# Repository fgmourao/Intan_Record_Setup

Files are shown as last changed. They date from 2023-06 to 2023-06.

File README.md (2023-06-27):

# A Fully Adapted Headstage With Custom Electrode Arrays Designed for Electrophysiological Experiments<br />

Front. Neurosci., 03 March 2022<br />
Sec. Neural Technology <br />
https://doi.org/10.3389/fnins.2021.691788<br />

Correspondence:<br />

Flávio Afonso Gonçalves Mourão, PhD<br />
Núcleo de Neurociências, Departamento de Fisiologia e Biofísica<br />
Instituto de Ciências Biológicas (ICB)<br /> 
Universidade Federal de Minas Gerais (UFMG)<br />
Av. Antônio Carlos, 6627 - CEP 31270-901- Campus Pampulha<br />
Belo Horizonte - MG - Brazil<br />
Fax: +55 31 3409-2924 Phone: +55 31 3409-2927<br />
Email:  mourao.fg@gmail.com / fagm@ufmg.br <br />

Márcio Flávio Dutra Moraes, PhD<br />
Núcleo de Neurociências, Departamento de Fisiologia e Biofísica<br />
Instituto de Ciências Biológicas (ICB)<br /> 
Universidade Federal de Minas Gerais (UFMG)<br />
Av. Antônio Carlos, 6627 - CEP 31270-901- Campus Pampulha<br />
Belo Horizonte - MG - Brazil<br />
Fax: +55 31 3409-2924 Phone: +55 31 3409-2930<br />
Email: mfdm@icb.ufmg.br <br />
<br />

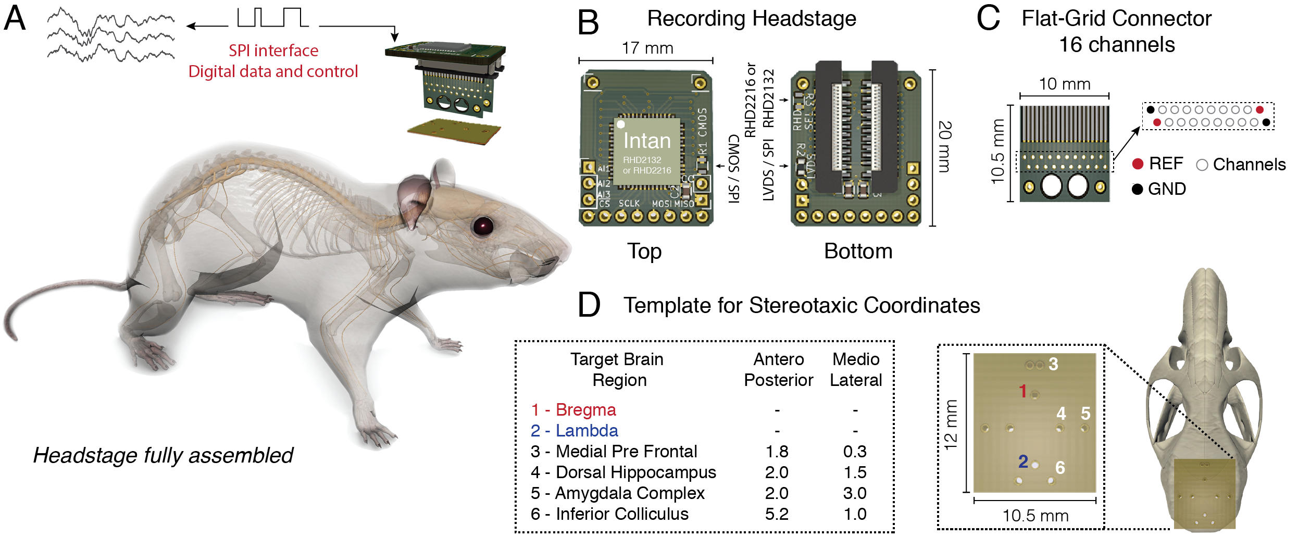
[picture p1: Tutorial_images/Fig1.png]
<br />

Headstage adapted from the Intan RHD headstage system with a flexible printed circuit (SMD/FPC) connector. A) Headstage fully assembled in real size. B) Top and bottom view of the headstage. Both the 2132 and 2216 Intan chips can be used according to the circuit configuration chosen. C) Flat-Grid connector board for sixteen channels designed to connect to the SMD/FPC connector. D) Fiber board punctured with small holes according to the chosen stereotaxic coordinates. A variable number of electrodes can be aligned and fixed from distinct dorsoventral configurations.

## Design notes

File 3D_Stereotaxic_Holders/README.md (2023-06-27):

# 3D Holders <br />

Support base to hold the fiber board <br />

https://github.com/fgmourao/Lab_Projects/blob/master/Intan%20Record%20Setup/Tutorial_images/1.png<br />

Support base to hold both the flat-grid connector and the fiber board <br />
https://github.com/fgmourao/Lab_Projects/blob/master/Intan%20Record%20Setup/Tutorial_images/0.png

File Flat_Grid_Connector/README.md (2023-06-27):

# Flat-Grid Connector <br />

V2 - Current Version<br />

https://github.com/fgmourao/Lab_Projects/blob/master/Intan%20Record%20Setup/Tutorial_images/Channels_Map_V2_Current_Version.png<br />

V1 - Old Version<br />

https://github.com/fgmourao/Lab_Projects/blob/master/Intan%20Record%20Setup/Tutorial_images/Channels_Map_V1_Old_Version.png<br />

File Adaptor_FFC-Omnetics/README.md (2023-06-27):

# Adapters

RHD 16-Channel Recording Headstages<br />

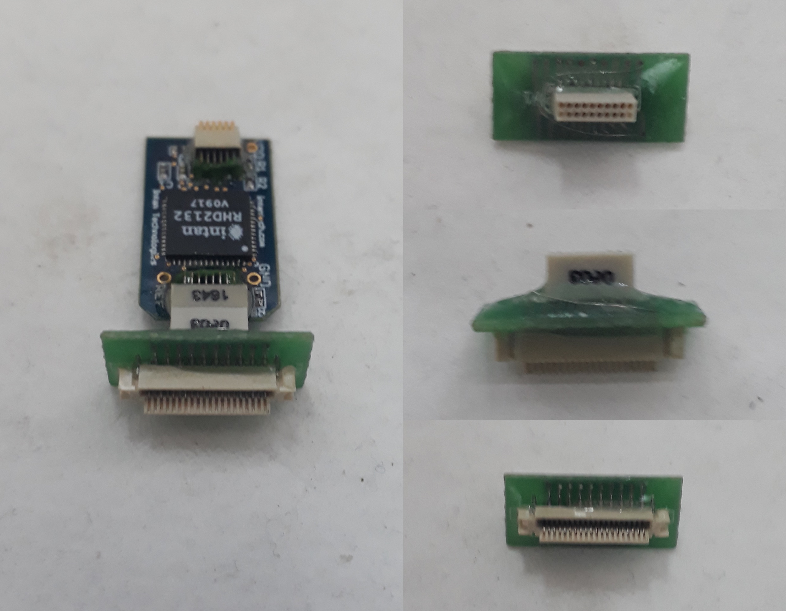
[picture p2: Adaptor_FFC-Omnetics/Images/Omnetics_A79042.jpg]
https://github.com/fgmourao/Lab_Projects/blob/master/Intan%20Record%20Setup/Adaptor_FFC-Omnetics/Images/Omnetics_A79042.jpg
<br />

RHD 32-Channel Recording Headstages<br />

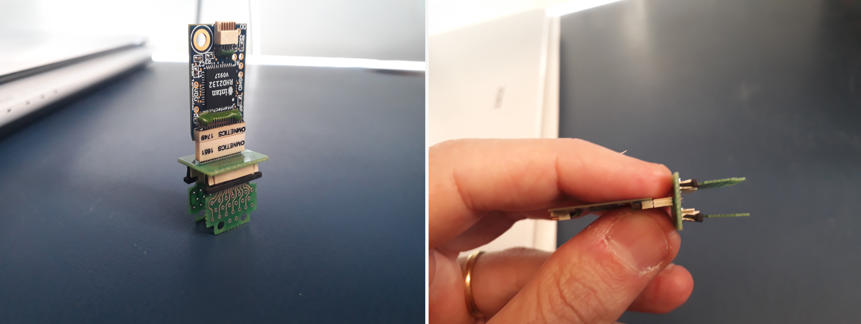
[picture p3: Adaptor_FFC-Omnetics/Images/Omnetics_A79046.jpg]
https://github.com/fgmourao/Lab_Projects/blob/master/Intan%20Record%20Setup/Adaptor_FFC-Omnetics/Images/Omnetics_A79046.jpg
<br />

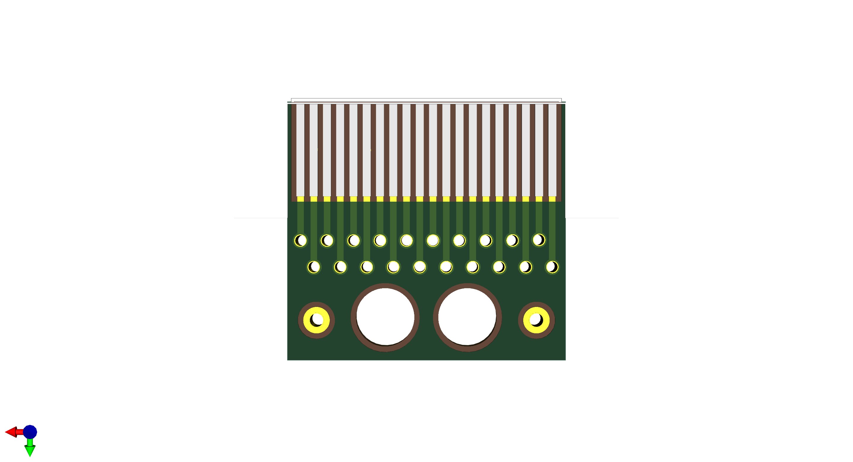
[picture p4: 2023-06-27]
Flat_Grid_Connector/V2/Schematic_PCB/Images/Flat_Grid_Small_V2.png

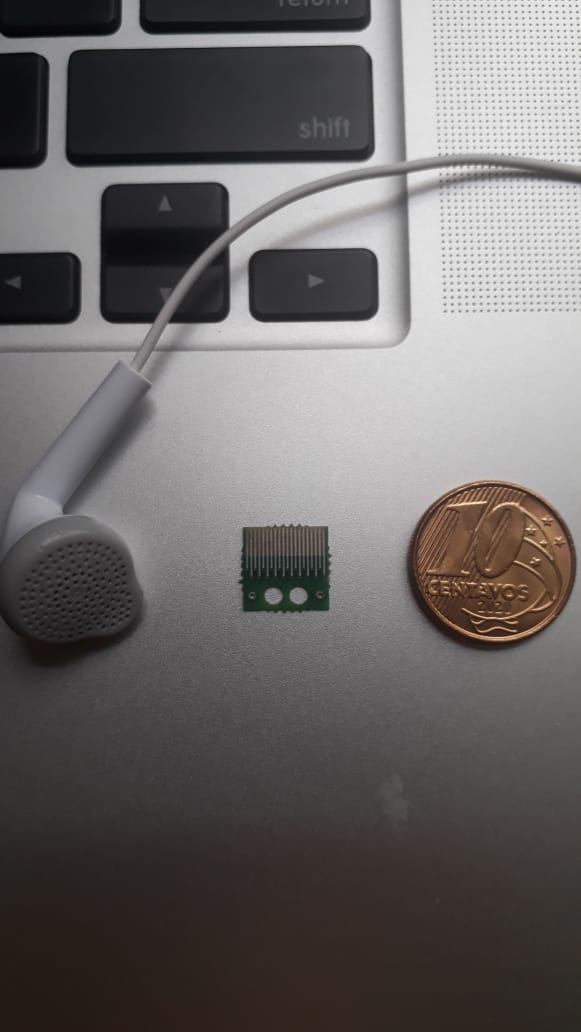
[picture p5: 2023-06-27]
Flat_Grid_Connector/V2/Schematic_PCB/Images/2021-03-30 at 17.20.01.png

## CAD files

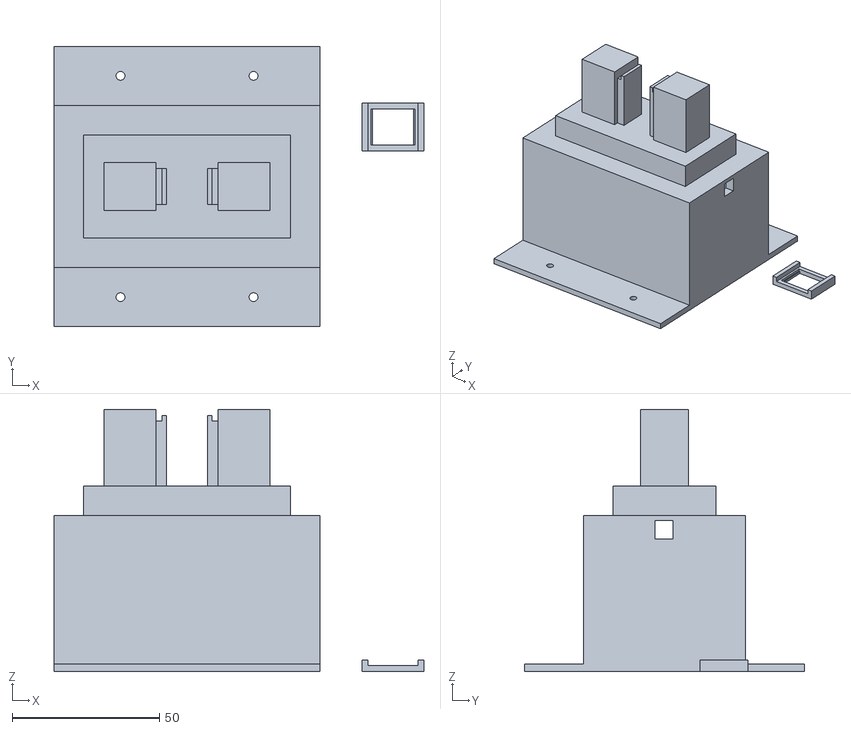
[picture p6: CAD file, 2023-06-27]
3D_Stereotaxic_Holders/Board_Stx_holder_rats.stl
125.4 x 95.0 x 88.9

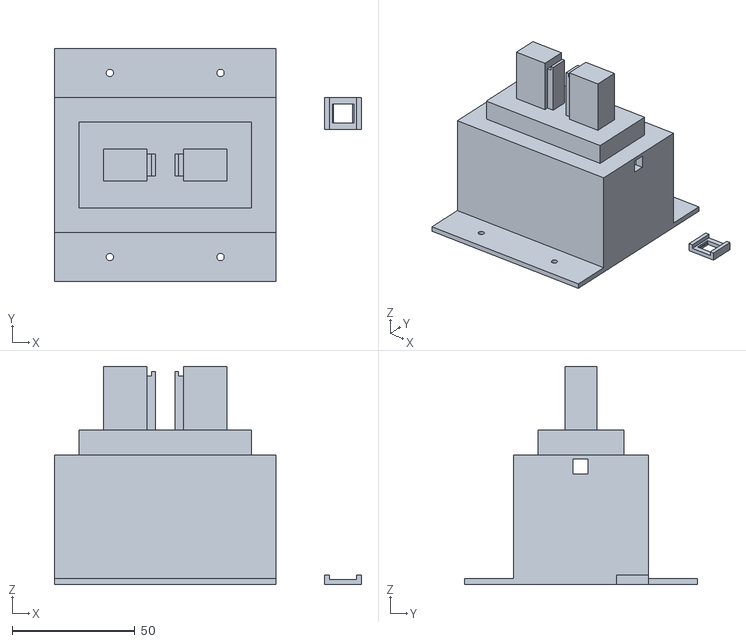
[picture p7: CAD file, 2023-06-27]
3D_Stereotaxic_Holders/Board_Stx_holder_mice.stl
125.1 x 95.0 x 88.9

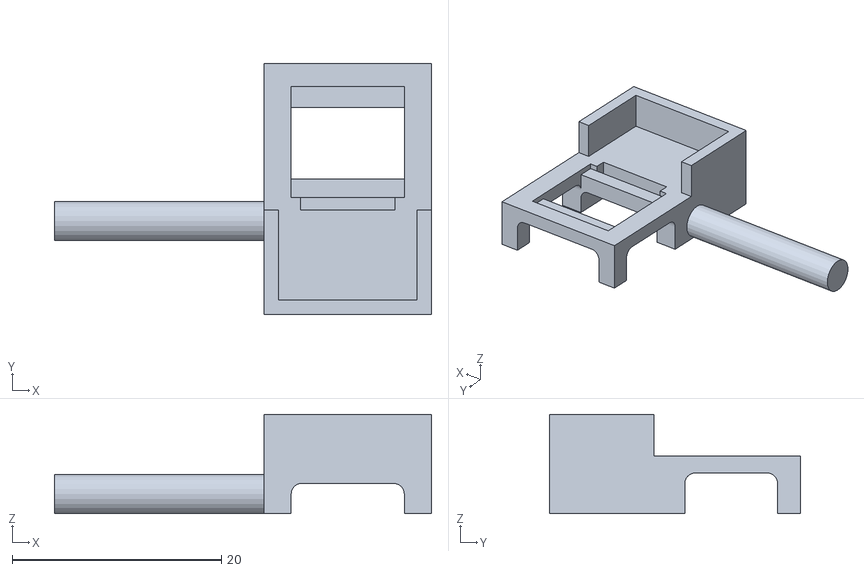
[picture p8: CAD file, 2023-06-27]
3D_Stereotaxic_Holders/Flat_template_holder.stl
36.0 x 24.0 x 9.50

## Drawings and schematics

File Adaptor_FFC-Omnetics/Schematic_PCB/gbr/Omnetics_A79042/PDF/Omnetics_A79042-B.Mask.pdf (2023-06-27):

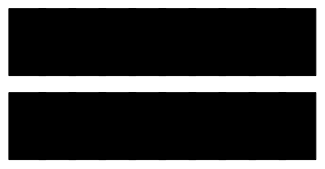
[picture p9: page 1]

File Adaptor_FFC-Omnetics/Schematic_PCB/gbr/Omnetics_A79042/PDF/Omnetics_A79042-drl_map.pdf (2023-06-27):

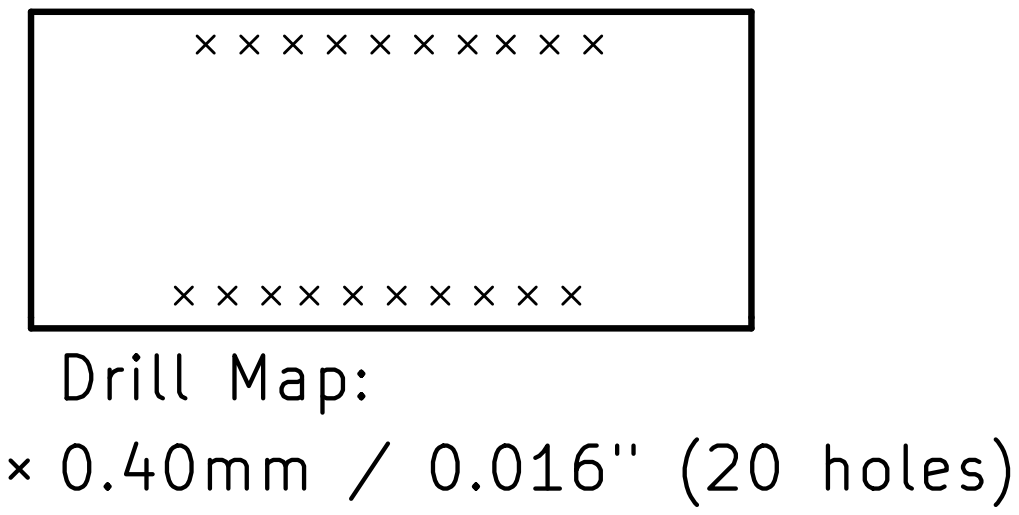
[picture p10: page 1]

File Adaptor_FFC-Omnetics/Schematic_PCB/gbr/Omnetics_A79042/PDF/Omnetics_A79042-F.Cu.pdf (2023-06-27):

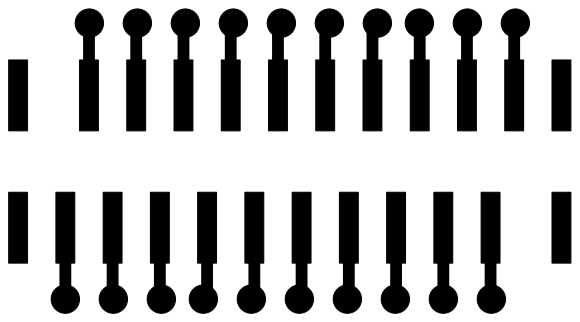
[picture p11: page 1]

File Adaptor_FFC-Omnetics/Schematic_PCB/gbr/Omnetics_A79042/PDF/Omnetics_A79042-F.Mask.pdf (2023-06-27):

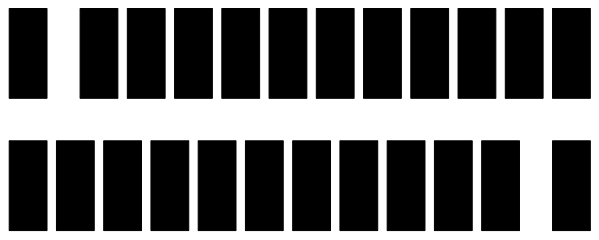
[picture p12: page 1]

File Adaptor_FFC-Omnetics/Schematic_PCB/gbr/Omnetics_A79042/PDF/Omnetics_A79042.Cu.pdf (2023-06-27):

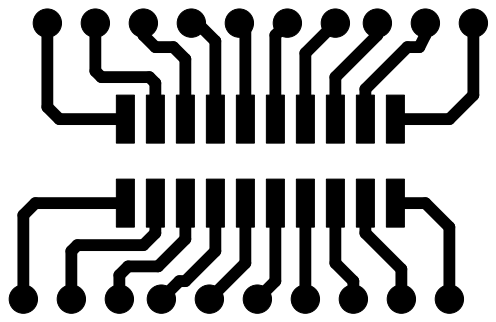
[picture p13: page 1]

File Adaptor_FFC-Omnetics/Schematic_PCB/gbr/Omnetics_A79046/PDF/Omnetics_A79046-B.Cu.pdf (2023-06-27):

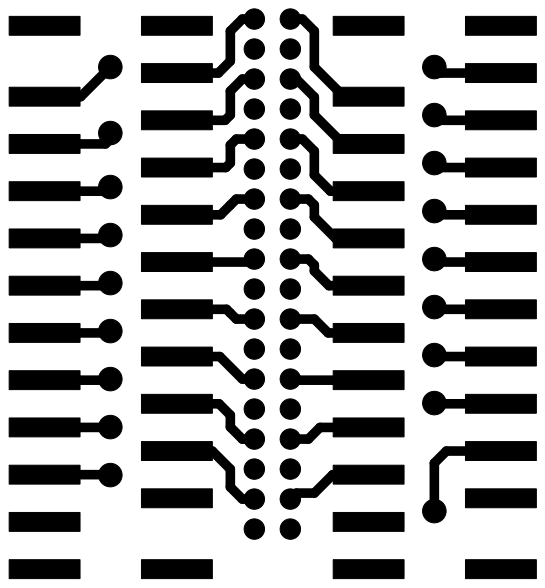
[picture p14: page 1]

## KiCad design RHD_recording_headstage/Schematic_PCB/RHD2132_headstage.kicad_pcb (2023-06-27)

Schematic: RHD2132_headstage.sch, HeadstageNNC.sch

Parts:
C1, C3: 100n; R_0603
C2: 10n; R_0603
J1, J2: FFCfemale20
J3: AuxInputs; Pin_Header_Straight_1x03_Pitch2.00mm
J4: SPI; JumperSPI2
J5: POWER; Pin_Header_Straight_1x02_Pitch2.00mm
J6, J7: Conn_01x01; Pin_Header_Straight_1x01_Pitch2.00mm
R1, R2, R3: 0; R_0603
U1: RHD2132_QFN; RHD2000-QFN56_8_X_8_LARGE

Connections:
/N$42: C2.1, U1.28 (ADC_REF)
/N$43: U1.27 (AUXOUT)
AUXIN1: J3.1, U1.14 (AUXIN1)
AUXIN2: J3.2, U1.15 (AUXIN2)
AUXIN3: J3.3, U1.16 (AUXIN3)
CH0: J1.3, U1.9 (IN0)
CH1: J1.4, U1.8 (IN1)
CH2: J1.5, U1.7 (IN2)
CH3: J1.6, U1.6 (IN3)
CH4: J1.7, U1.5 (IN4)
CH5: J1.8, U1.4 (IN5)
CH6: J1.9, U1.3 (IN6)
CH7: J1.10, U1.2 (IN7)
CH8: J1.11, U1.1 (IN8)
CH9: J1.13, U1.56 (IN9)
CH10: J1.15, U1.55 (IN10)
CH11: J1.17, U1.54 (IN11)
CH12: J1.16, U1.53 (IN12)
CH13: J1.18, U1.52 (IN13)
CH14: J1.14, U1.51 (IN14)
CH15: J1.12, U1.50 (IN15)
CH16: J2.13, U1.49 (IN16)
CH17: J2.17, U1.48 (IN17)
CH18: J2.15, U1.47 (IN18)
CH19: J2.18, U1.46 (IN19)
CH20: J2.16, U1.45 (IN20)
CH21: J2.14, U1.44 (IN21)
CH22: J2.12, U1.43 (IN22)
CH23: J2.11, U1.42 (IN23)
CH24: J2.10, U1.41 (IN24)
CH25: J2.9, U1.40 (IN25)
CH26: J2.8, U1.39 (IN26)
CH27: J2.7, U1.38 (IN27)
CH28: J2.6, U1.37 (IN28)
CH29: J2.5, U1.36 (IN29)
CH30: J2.4, U1.35 (IN30)
CH31: J2.3, U1.34 (IN31)
GND: C1.2, C2.2, C3.2, J1.1, J1.20, J2.1, J2.20, J5.1, R1.1, R3.1, U1.11 (GND1), U1.12 (GND2), U1.17 (GND3), U1.29 (GND4), U1.32 (VESD), U1.CENT (CTR)
MISO+: J4.8, U1.25 (MISO+)
MISO-: J4.7, U1.24 (MISO-)
MOSI+: J4.6, U1.23 (MOSI+)
MOSI-: J4.5, U1.22 (MOSI-)
unnamed: R1.2, R2.2, U1.30 (LVDS_EN)
REF_ELECTRODE: J1.2, J1.19, J2.2, J2.19, R3.2, U1.10 (REF_ELEC)
SCLK+: J4.4, U1.21 (SCLK+)
SCLK-: J4.3, U1.20 (SCLK-)
VCC: C1.1, C3.1, J5.2, R2.1, U1.13 (VDD1), U1.26 (VDD2), U1.31 (VDD3)
~CS~+: J4.2, U1.19 (~CS~+)
~CS~-: J4.1, U1.18 (~CS~-)

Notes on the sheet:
RHD2132 Intan Chip
FFC Connectors
Select between LVDS and CMOS
Jumpers
Mechanical support
LVDS
CMOS
Select between RHD2216 and RHD2132
This resistor must be soldered when using RHD2216.
Unconnected

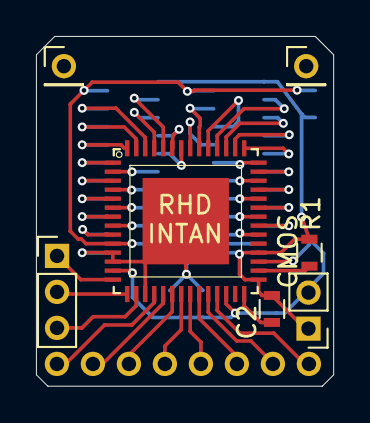
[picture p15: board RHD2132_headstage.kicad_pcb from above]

Board: 4 copper layers, 16.5 x 19.4 mm, 14 parts (0 on the bottom side), 48 nets.

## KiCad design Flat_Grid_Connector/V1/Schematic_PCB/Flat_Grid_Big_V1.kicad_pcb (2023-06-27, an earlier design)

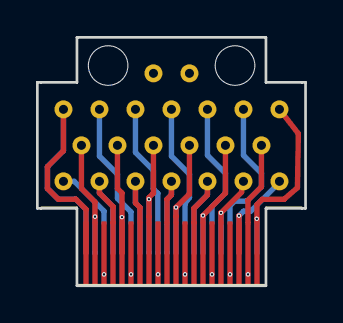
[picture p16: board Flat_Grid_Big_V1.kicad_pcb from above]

Board: 2 copper layers, 14.9 x 13.8 mm, 3 parts (1 on the bottom side), 20 nets.

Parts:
Edge1, Edge2: Conn_01x20; FFCmale20_semvias
Holes1: Conn_01x20; FFCmalePINarray

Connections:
unnamed: Edge1.1, Edge2.20, Holes1.1
unnamed: Edge1.2, Edge2.19, Holes1.2
unnamed: Edge1.3, Edge2.18, Holes1.3
unnamed: Edge1.4, Edge2.17, Holes1.4
unnamed: Edge1.5, Edge2.16, Holes1.5
unnamed: Edge1.6, Edge2.15, Holes1.6
unnamed: Edge1.7, Edge2.14, Holes1.7
unnamed: Edge1.8, Edge2.13, Holes1.8
unnamed: Edge1.9, Edge2.12, Holes1.9
unnamed: Edge1.10, Edge2.11, Holes1.10
unnamed: Edge1.11, Edge2.10, Holes1.11
unnamed: Edge1.12, Edge2.9, Holes1.12
unnamed: Edge1.13, Edge2.8, Holes1.13
unnamed: Edge1.14, Edge2.7, Holes1.14
unnamed: Edge1.15, Edge2.6, Holes1.15
unnamed: Edge1.16, Edge2.5, Holes1.16
unnamed: Edge1.17, Edge2.4, Holes1.17
unnamed: Edge1.18, Edge2.3, Holes1.18
unnamed: Edge1.19, Edge2.2, Holes1.19
unnamed: Edge1.20, Edge2.1, Holes1.20

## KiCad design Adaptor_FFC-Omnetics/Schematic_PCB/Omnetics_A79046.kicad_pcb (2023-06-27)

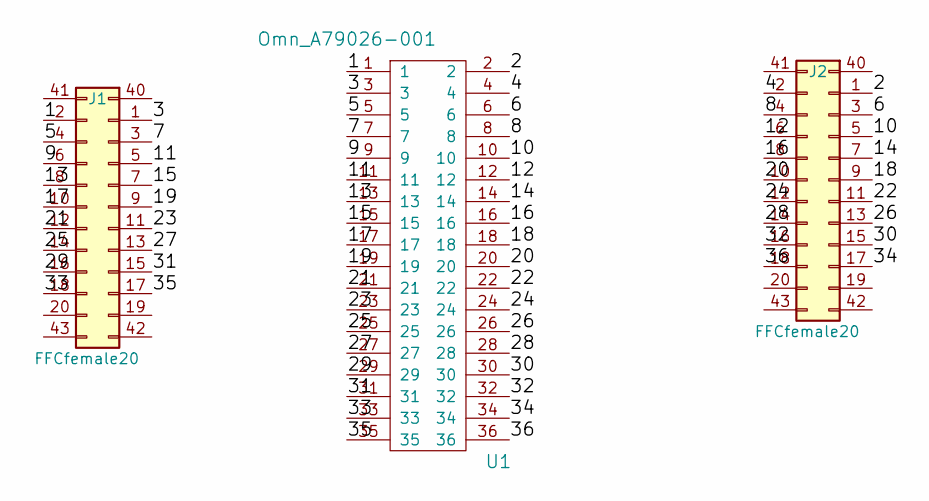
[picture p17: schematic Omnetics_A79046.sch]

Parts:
J1, J2: FFCfemale20
U1: Omn_A79026-001; Omn_A79026_pin

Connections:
/1: J1.2, U1.1
/2: J2.1, U1.2
/3: J1.1, U1.3
/4: J2.2, U1.4
/5: J1.4, U1.5
/6: J2.3, U1.6
/7: J1.3, U1.7
/8: J2.4, U1.8
/9: J1.6, U1.9
/10: J2.5, U1.10
/11: J1.5, U1.11
/12: J2.6, U1.12
/13: J1.8, U1.13
/14: J2.7, U1.14
/15: J1.7, U1.15
/16: J2.8, U1.16
/17: J1.10, U1.17
/18: J2.9, U1.18
/19: J1.9, U1.19
/20: J2.10, U1.20
/21: J1.12, U1.21
/22: J2.11, U1.22
/23: J1.11, U1.23
/24: J2.12, U1.24
/25: J1.14, U1.25
/26: J2.13, U1.26
/27: J1.13, U1.27
/28: J2.14, U1.28
/29: J1.16, U1.29
/30: J2.15, U1.30
/31: J1.15, U1.31
/32: J2.16, U1.32
/33: J1.18, U1.33
/34: J2.17, U1.34
/35: J1.17, U1.35
/36: J2.18, U1.36

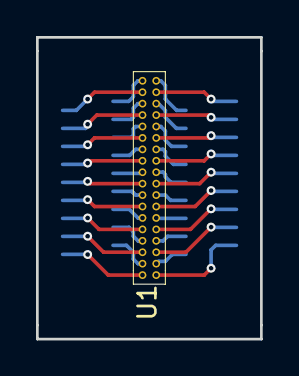
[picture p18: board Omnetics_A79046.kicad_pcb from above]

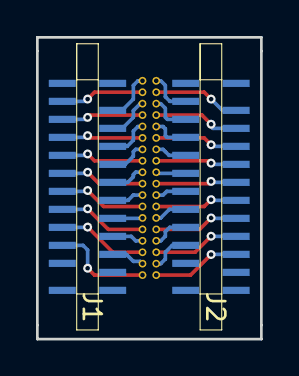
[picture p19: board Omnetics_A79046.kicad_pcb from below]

Board: 2 copper layers, 12.4 x 16.8 mm, 3 parts (2 on the bottom side), 36 nets.

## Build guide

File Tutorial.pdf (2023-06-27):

A fully adapted headstage for electrophysiological experiments with custom and scalable electrode arrays to record widely distributed brain regions.

Supplementary Material – Tutorials

Authors: Flávio Afonso Gonçalves Mourãoa

, Leonardo de Oliveira Guarnieri ab, Paulo Aparecido Amaral Júnior ab, Vinícius Rezende Carvalho ab

, Eduardo Mazoni Andrade Marçal Mendes ab, Márcio Flávio Dutra Moraes a
a. Núcleo de Neurociências, Departamento de Fisiologia e Biofísica, Instituto de Ciências Biológicas (ICB), Universidade Federal de Minas Gerais (UFMG). Av. Antônio Carlos, 6627 - CEP 31270-901. Belo Horizonte, Minas Gerais, Brazil.
b. Programa de Pós-Graduação em Engenharia Elétrica, Departamento de Engenharia Eletrônica (DELT), Escola de Engenharia, Universidade Federal de Minas Gerais (UFMG). Av. Antônio Carlos, 6627 - CEP 31270-901. Belo Horizonte, Minas Gerais, Brazil.

Correspondence:

Flávio Afonso Gonçalves Mourão, PhD Email: fagm@ufmg.br

Márcio Flávio Dutra Moraes, PhD Email: mfdm@icb.ufmg.br

2021

Recording Headstage

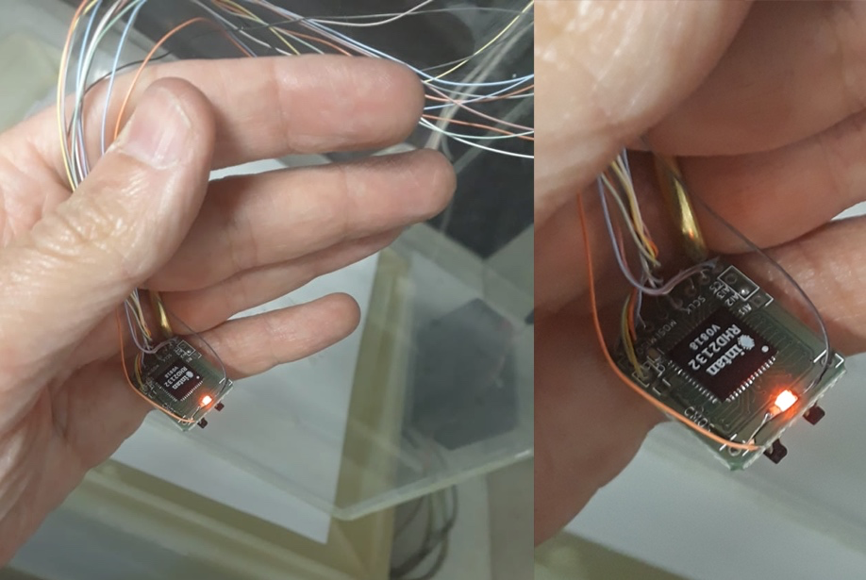
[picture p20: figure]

* Led is not in the original project

Component | Specification | Supplier | Price | Quantity | Link
FPC connector (Flexible Printed Circuits) | SMD vertical type 0.5mm pitch 2mm height | mktechnic | $0.79(un) | 2 | https://cutt.ly/Xx55qQE
RHD2132 amplifier chip | 32-channel unipolar inputs and common reference | Intan Technologies | $390 (un) | 1 | https://cutt.ly/Yx6qief
RHD2216 amplifier chip | 16-channel differential inputs | Intan Technologies | $260 (un) | 1 | https://cutt.ly/Yx6qief
Resistor | SMD – 0 W | Digikey | $0.22(un) | 1 | https://www.digikey.com
Capacitor | SMD – 10 nF | Digikey | $0.17(un) | 1 | https://www.digikey.com
Capacitor | SMD – 100 nF | Digikey | $0.17(un) | 2 | https://www.digikey.com

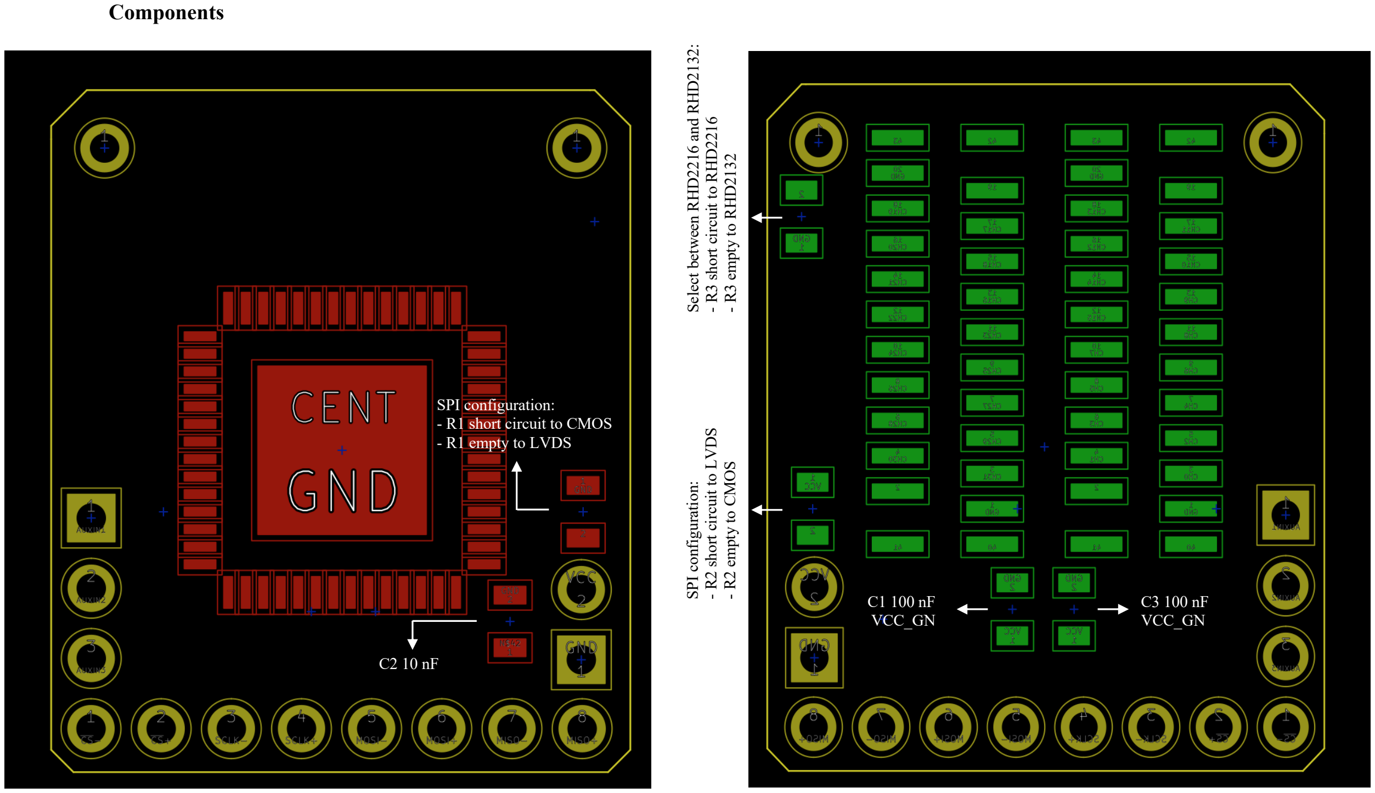
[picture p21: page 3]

Components

SPI configuration: - R1 short circuit to CMOS - R1 empty to LVDS

C2 10 nF

Select between RHD2216 and RHD2132:

- R3 short circuit to RHD2216
- R3 empty to RHD2132

SPI configuration:

- R2 short circuit to LVDS
- R2 empty to CMOS

C1 100 nF
VCC_GN

C3 100 nF
VCC_GN

Handmade cable

We strongly recommend the following tutorial:

- https://open-ephys.atlassian.net/wiki/spaces/OEW/pages/491587/Fine+wire+tether
Component | Specification | Supplier | Price | Quantity | Link
Omnetics Polarized PZN | Straight Thru-Hole (Type DD) 12 contacts | Omnetics Connector Corporation | on request ~$40 (un) | 1 | https://cutt.ly/FcqiCNQ
Micro bare copper wire | CZ 1187 wire series | Cooner Wire | on request | 1 | https://cutt.ly/lcqo9Pz

However, in our adapted board, each contact needs to be checked

Wiring diagram:

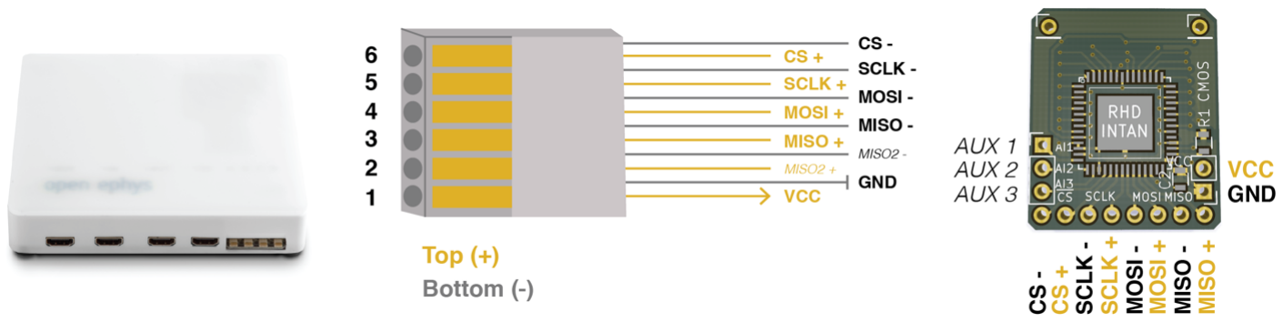
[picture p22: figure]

Flat-Grid Connector – V2 – Current Version

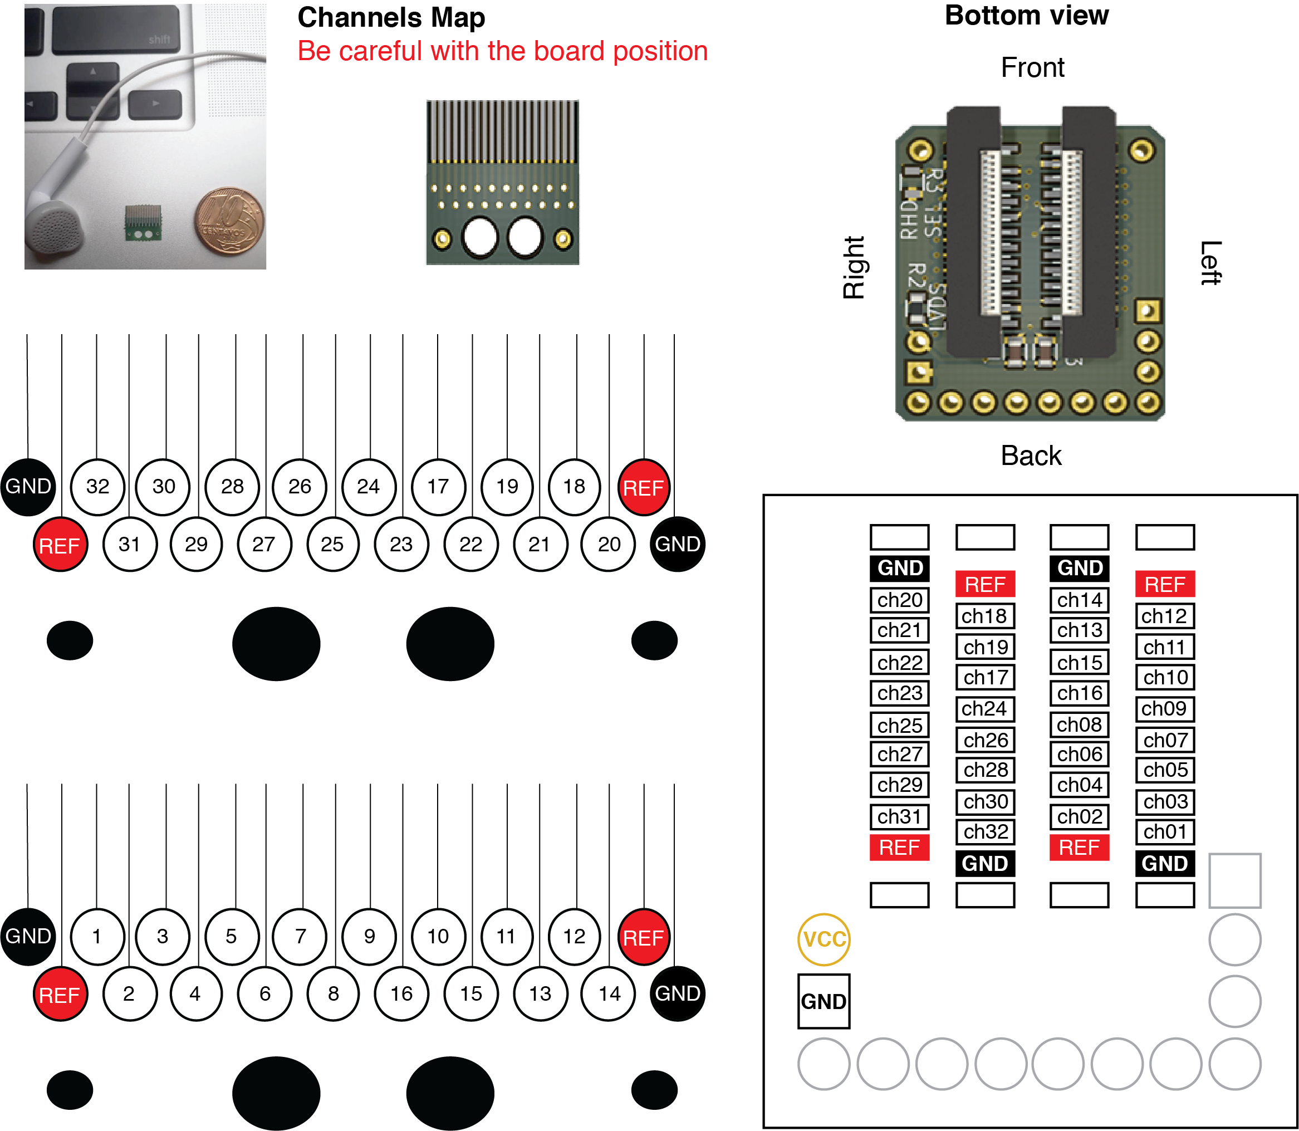
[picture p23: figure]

Component | Specification | Supplier | Price | Quantity | Link
Stainless steel wire | 0.127 mm internal diameter, teflon-coated. 100 feet. Model 7914 | A-M Systems Inc | $140 (un) | 1 | https://cutt.ly/5x6eIoR
Tungsten microwires | 99.5% S-Formvar 50 µm ID | California Fine Wire Co. | on request | - | https://cutt.ly/FbJxLBi
Silver paint | 1 troy oz. (31.1g) | SPI SuppliesⓇ | ~$50 (un) | 1 | https://cutt.ly/Ox6sup1
Thermosetting polymer | 5 minute Epoxy | Devcon | ~$20 (un) | 1 | https://cutt.ly/Zx6ltrEhttps://cutt.ly/mx6zobJhttps://cutt.ly/Rx6zFZZ
Scissors | Tungsten Carbide 3.5 inches | Dr. Slick Co. | ~$30 (un) | 1 | https://www.drslick.com

Flat-Grid Connector – V1 – Old Version

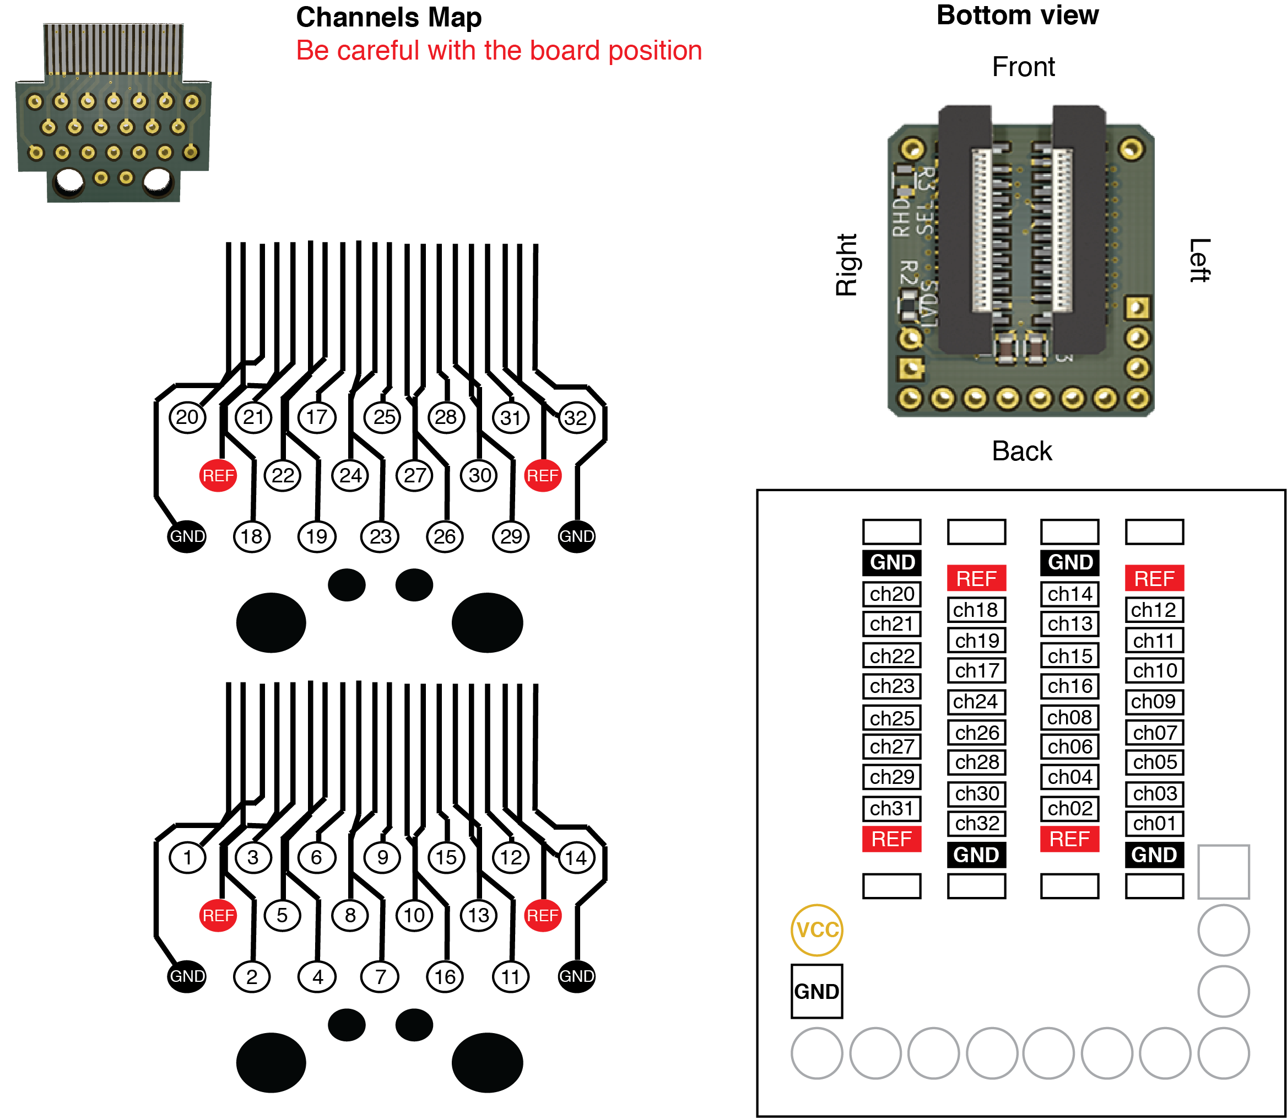
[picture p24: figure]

SMD/FPC connector ß à Omnetics
Adapters for the original RHD headstage
Component | Specification | Supplier | Price | Quantity | Link
FPC connector (Flexible Printed Circuits) | SMD vertical type 0.5mm pitch 2mm height | mktechnic | $0.79(un) | 2 | https://cutt.ly/Xx55qQE
Omnetics Neuro Nano Strip | A79042-001 NPD-18-VV-GS | Omnetics Connector Corporation | on request ~$60 (un) | 1 | https://cutt.ly/UcqDO66
Omnetics Neuro Nano Strip | A79046-001 NPD-36-DD-GS | Omnetics Connector Corporation | on request ~$90 (un) | 1 | https://cutt.ly/UcqDO66

RHD 16-Channel Recording Headstages

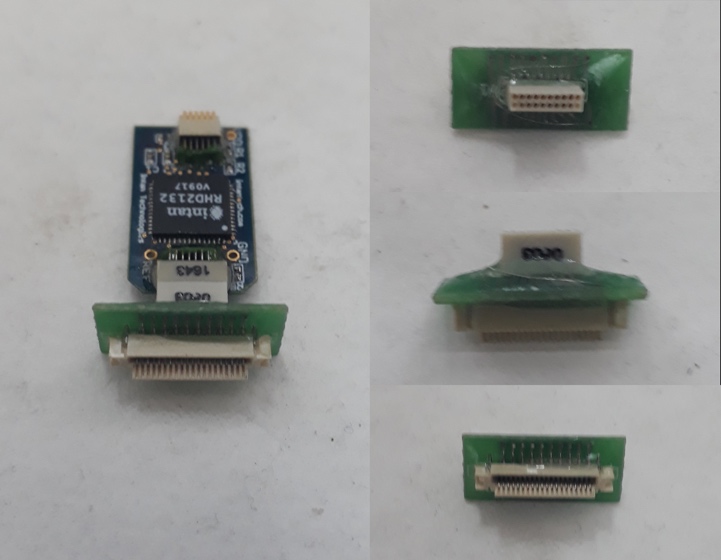
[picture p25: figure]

RHD 32-Channel Recording Headstages

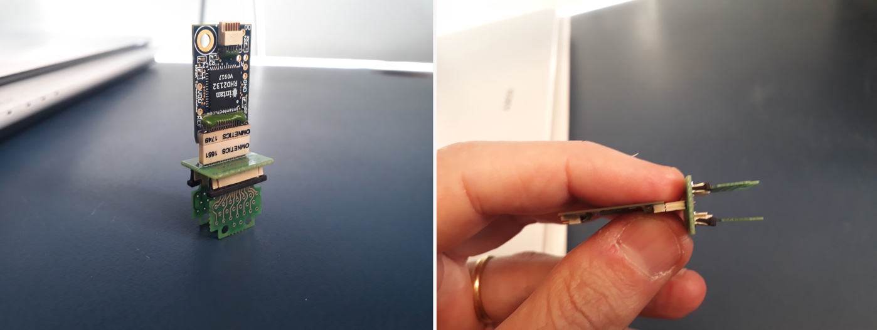
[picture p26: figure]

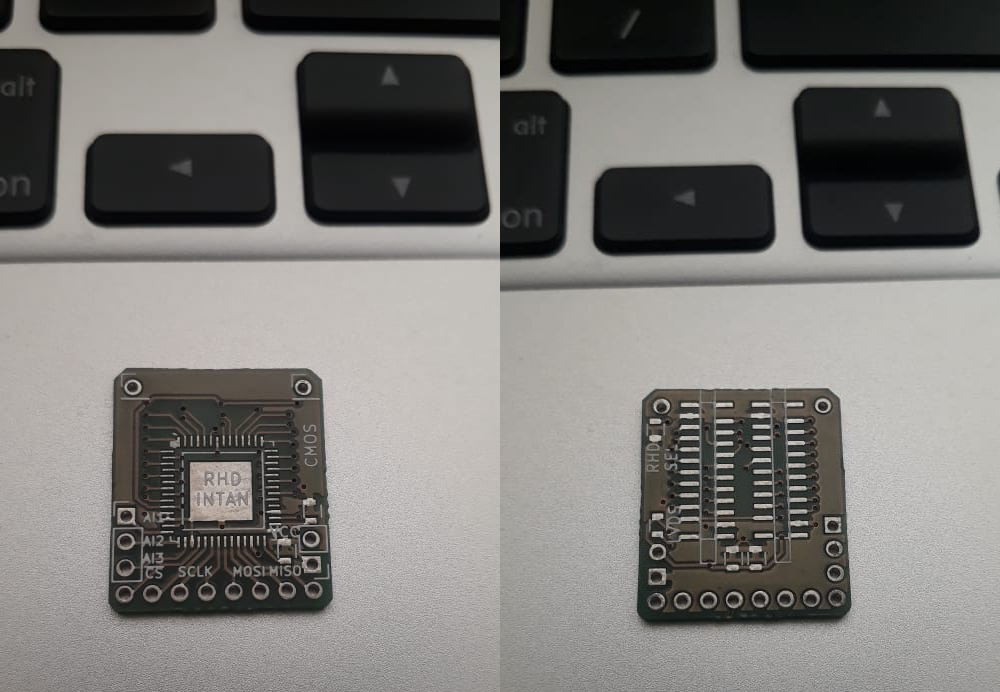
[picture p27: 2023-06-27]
Tutorial_images/headstage2.png

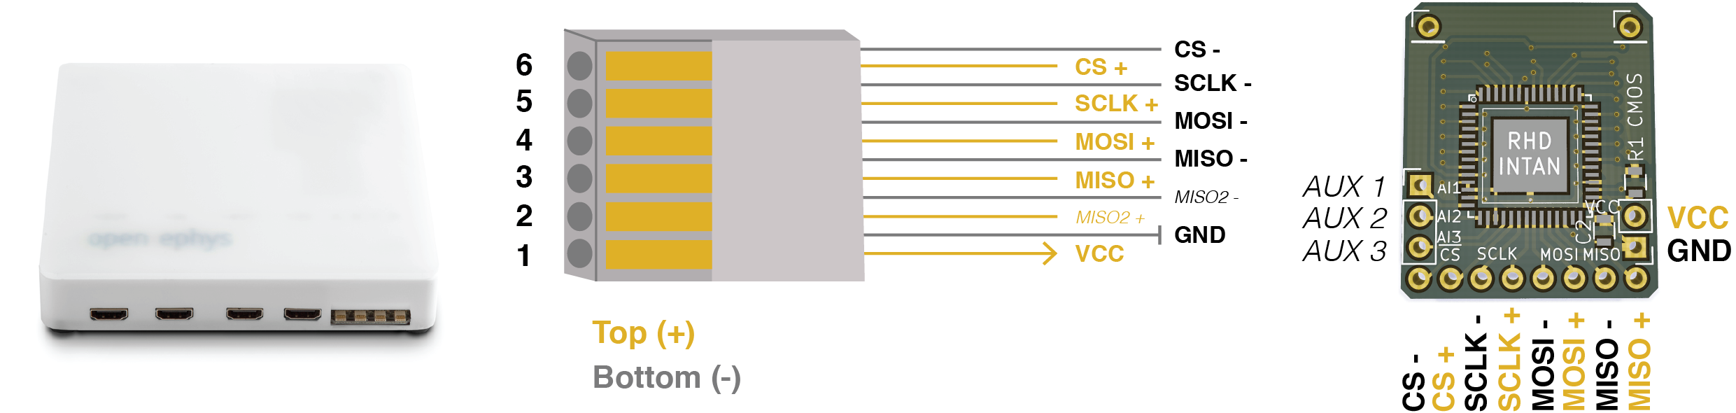
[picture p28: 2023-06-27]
Tutorial_images/cable-01.png

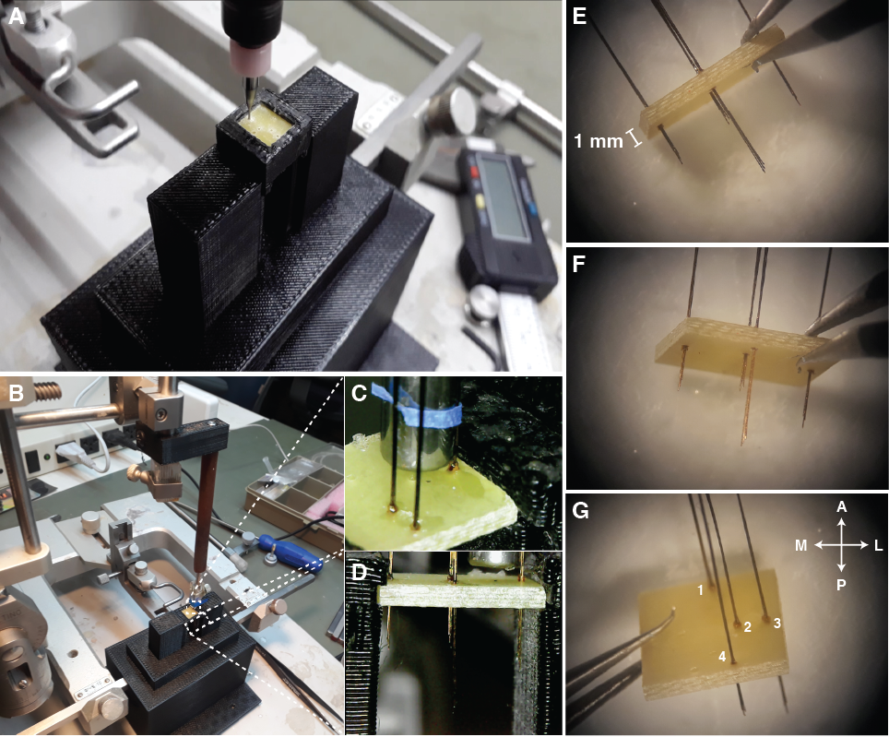
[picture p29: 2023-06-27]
Tutorial_images/Fig3.png

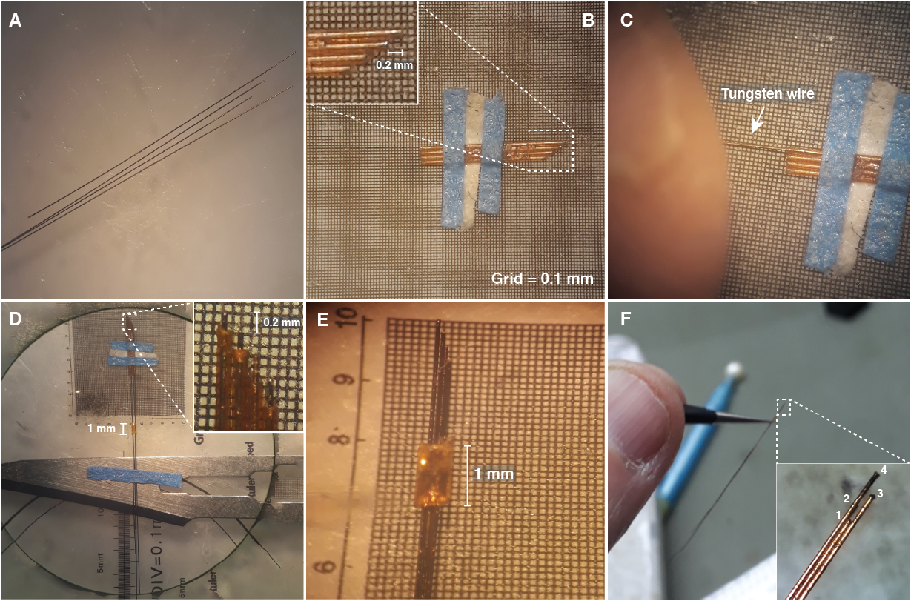
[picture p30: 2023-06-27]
Tutorial_images/Fig2.png
